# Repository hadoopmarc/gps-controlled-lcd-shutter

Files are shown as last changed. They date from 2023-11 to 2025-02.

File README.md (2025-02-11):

# gps-controlled-lcd-shutter

## Introduction

The GPS-controlled LCD shutter is used for photography of bright meteors. Traditionally, periodic shutters are applied in multi-station photography for aiding the calculation of the atmospheric trajectory and velocity of a meteoroid. The controlling system documented in this git repository adds 1 Hz time markers to the waveform driving an LCD shutter. These markers are synchronized with the highly accurate time signal of a GPS module. The markers function as additional reference points for comparing records from multiple stations. The technique was pioneered by the Ondřejov Observatory in the Czech Republic, see: [https://link.springer.com/article/10.1007/s11038-017-9511-z](https://link.springer.com/article/10.1007/s11038-017-9511-z).

The required pattern for obstructing the light passing through the camera lens is visible from the photograph below (courtesy of the Astronomical Institute of the Academy of Sciences of the Czech Republic).

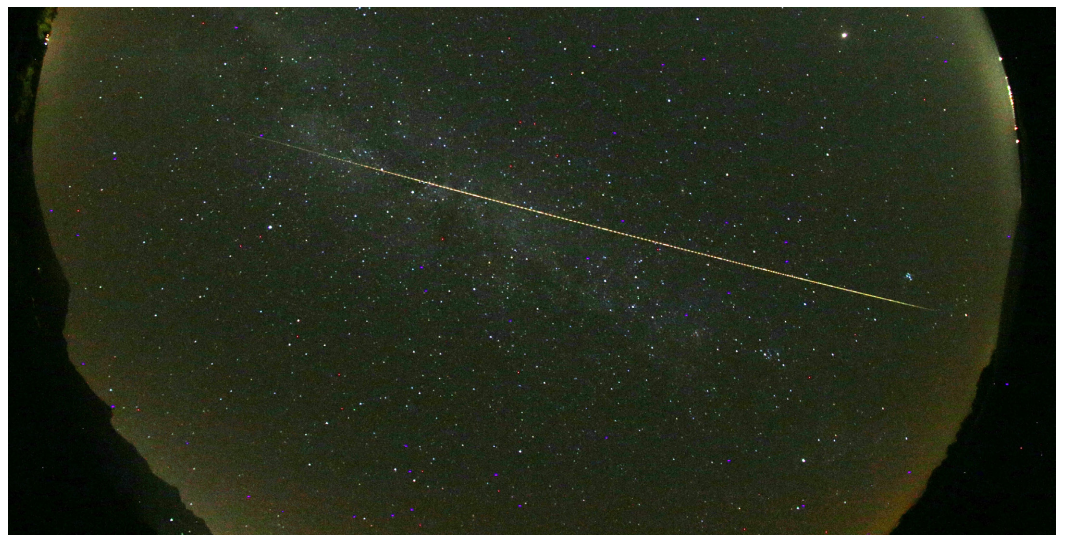
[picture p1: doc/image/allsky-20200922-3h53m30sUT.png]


## Reference design

When using an LCD shutter to realize the required pattern one needs an LCD opaqueness waveform represented as signal I in the figure below. The end of a long part of the meteor trail - or the rising edge of the first pulse of a pulse train in signal I - occurs a N + 2/32 seconds exactly.

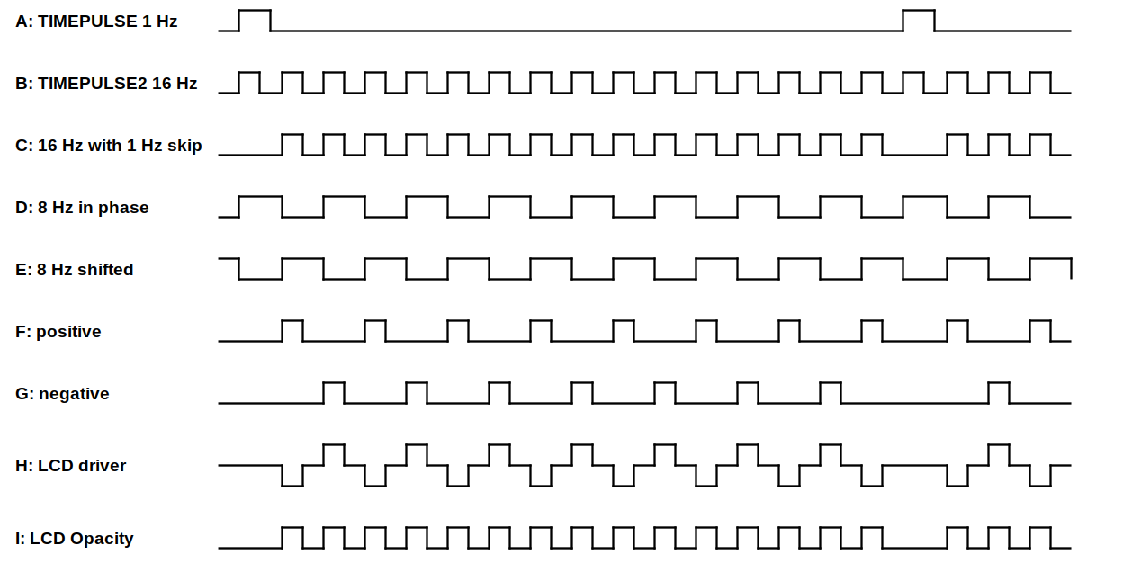
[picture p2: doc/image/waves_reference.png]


The waveform required to drive the LCD shutter has both a 16 Hz signature for the periodic interruptions and a 1 Hz signature for the second markers. The Ublox Neo-M8T SoC is able to deliver both signals with high precision on its TIMEPULSE and TIMEPULSE2 outputs (signals A and B). Because of this high precision, the design with Neo-M8T is designated as the reference design.

Apart from the frequencies involved, there are additional requirements for driving an LCD shutter:

- although an LCD shutter becomes opaque when a voltage is put on it in either direction, it is advised to change the polarity of the applied voltage with each cycle to avoid degradation of the display (signal H)
- upon switching, the shutter draws a relatively high peak current of 28 mA during a short time

These requirements make that the LCD-shutter is better not driven by logical outputs directly. Rather, the reference design applies opamps to convert the logical signals into +/- 12V with a sufficiently low output impedance, see the top part of the electronic circuit below. The final opamp adds the inverted signal F to the signal G to create signal H. The electronic circuit for the final opamp includes a variable resistor RV1 to set the "inactive" output voltage to exactly 0V for maximum transparency of the LCD shutter.

For converting signals A and B into signals F and G, a few CMOS NAND ports and a D-flipflop are applied. Note that the 1 Hz signal is also fed into the reset port of the flipflop to have the edges of the 8 Hz signals D and E coincide with the rising edge of the 1 Hz signal.

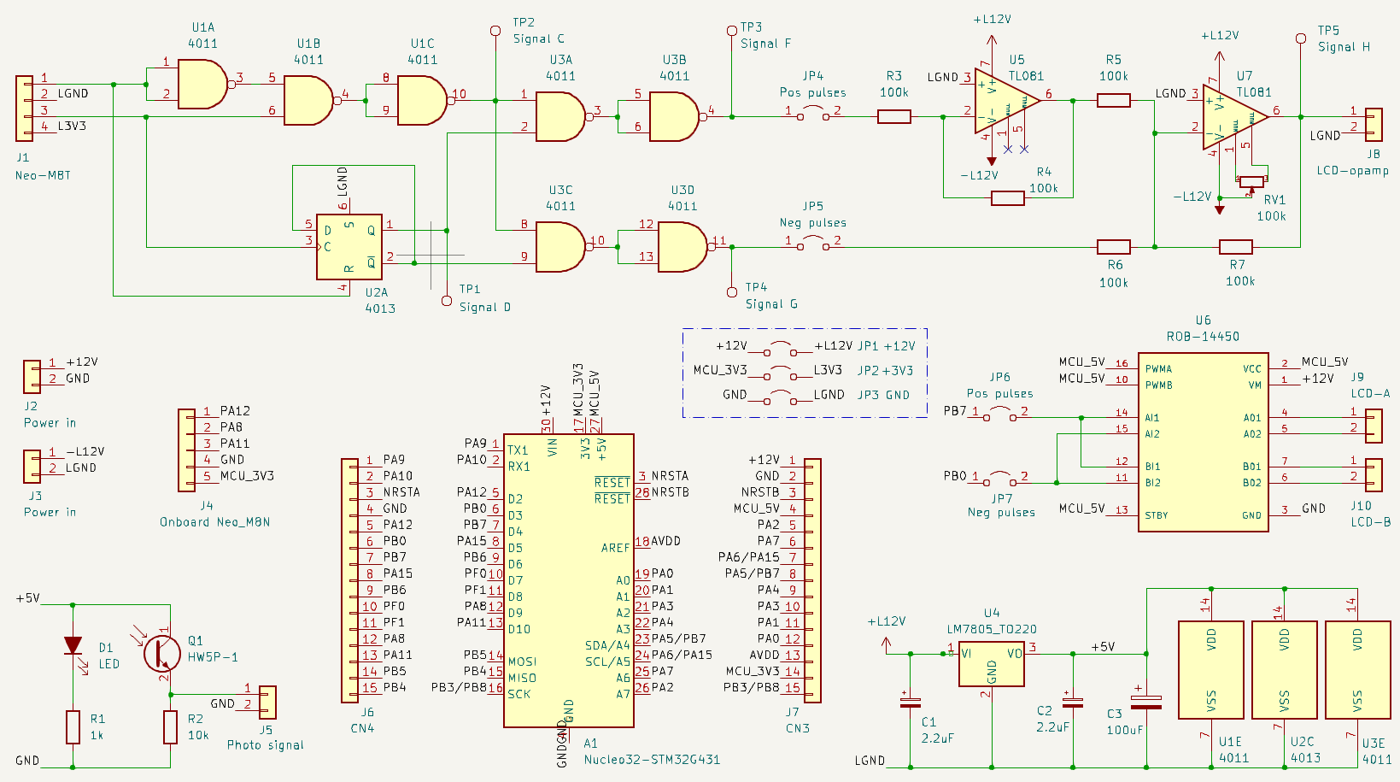
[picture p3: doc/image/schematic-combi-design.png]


## Optimized design

Although the reference design guarantees a high timing precision, it has significant drawbacks:

- the Neo-M8T is 10 times more expensive than its more nimble Neo-M8N sibling and dominates the production costs of the system
- the Neo-M8T is not available on a breakout board with the TIMEPULSE and TIMEPULSE2 output signals, so this requires high-precision soldering on 1 mm spaced SMD output pins
- the opamp circuit requires positive and negative power supplies
- the opamp circuit is hard to get stable and can only barely supply the peak current of the LCD shutter

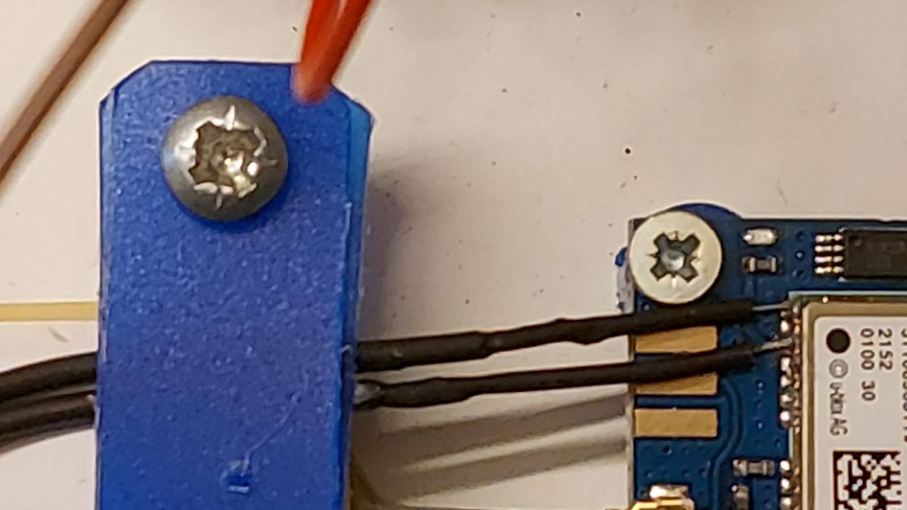
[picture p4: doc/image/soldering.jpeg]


Presenting the reference design to two different audiences resulted in valuable feedback to optimize the design:

- the required waveforms can also be produced by a microcontroller such as the Arduino board, by only using the 1 Hz output signal of a GPS module and using the internal, less precise clock of the microcontroller to obtain the 16 Hz timing information (see [this contribution to the repository](https://github.com/hadoopmarc/gps-controlled-lcd-shutter/commit/29299f46e7cd1bd2d8dd73f03644191cccfc6193)). Now, the cheaper Neo-M8N suffices to provide the 1 Hz timing data.
- an H-bridge module - often used to drive a DC motor - seems also suitable to drive the LCD shutter. An H-bridge only requires a positive power supply and can deliver high output currents.

This feedback resulted in the final optimized design, displayed in the electronic circuit diagram below. As the LCD shutter is already driven with a 16 Hz frequency, the H-bridge PWM duty cycle has a fixed setting of 100%. An H-bridge has two modes for a low output voltage, see the truth table below: short circuit the output pins ("Short brake" in motor terms) or disconnect the output pins ("Free run until frictional stop" in motor terms). It turns out that the LCD shutter needs the short circuit so that it can release its internal charge/polarity and become transparent as fast as possible.

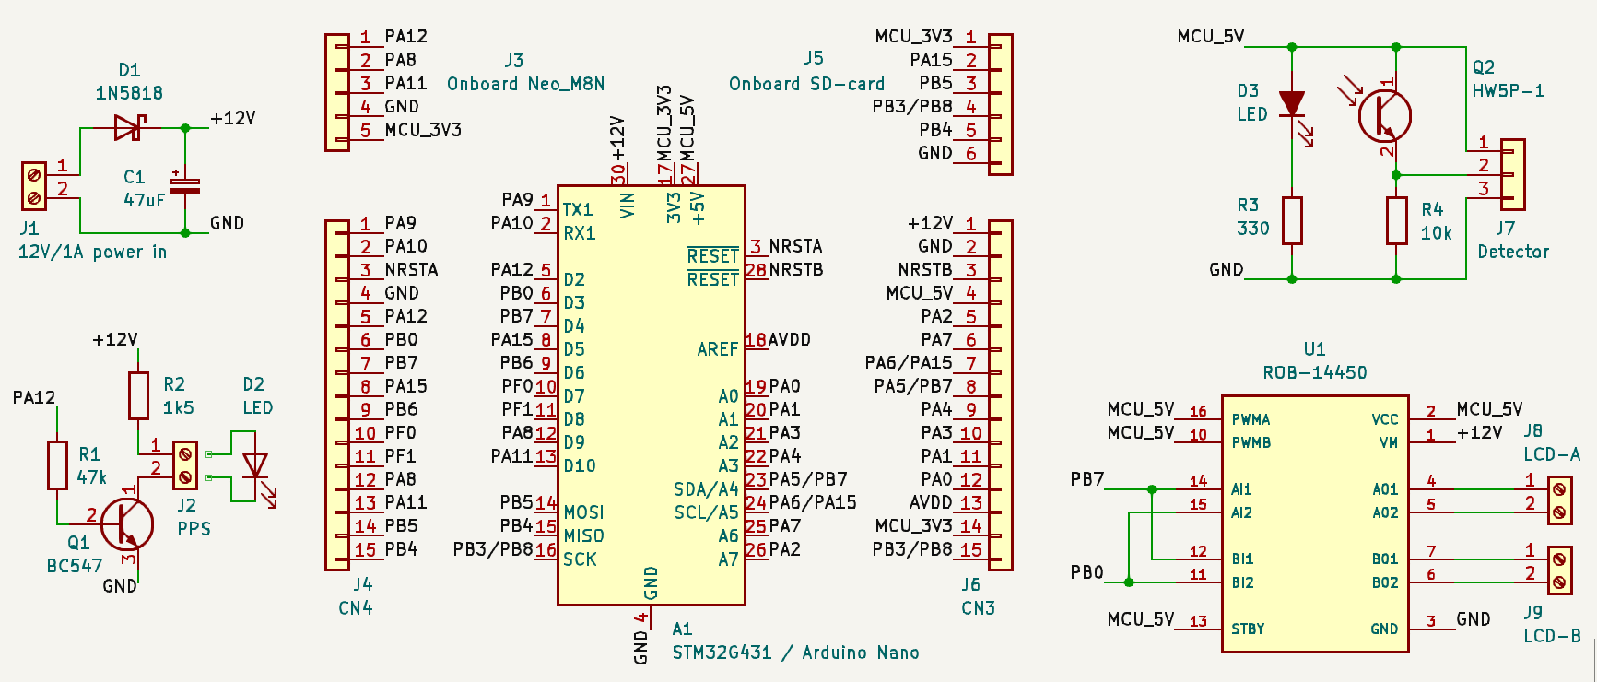
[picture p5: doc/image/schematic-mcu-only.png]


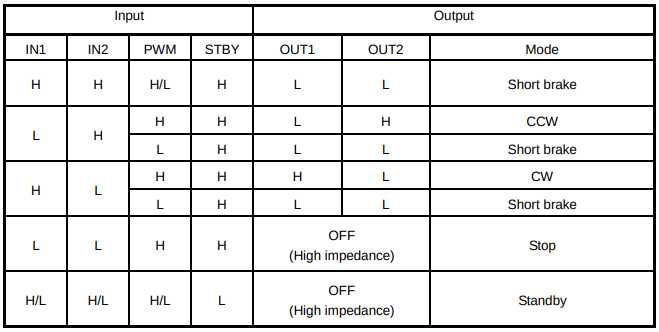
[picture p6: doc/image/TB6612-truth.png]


The required input signals to the H-bridge are displayed in the waveform diagram below. Also in this design, the end of a long segment in the meteor trail - or the rising edge of the first pulse of a pulse train in the LCD opacity signal - occurs a N + 2/32 seconds exactly. After all, the long segment in the meteor trail has a duration of 3/32 second, but the GPS second pulse occurs after 1/32 second from the start of the long segment.

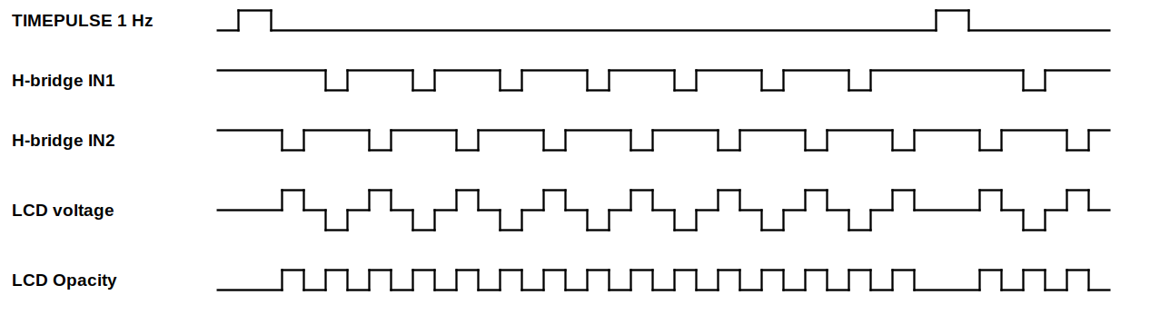
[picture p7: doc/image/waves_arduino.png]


## Validation of the designs

Proper operation of both designs can be validated with an [Arduino Oscilloscope](./doc/arduino-scope.md) and the small LED + phototransistor setup of the lower left part of the electronic circuit diagram.

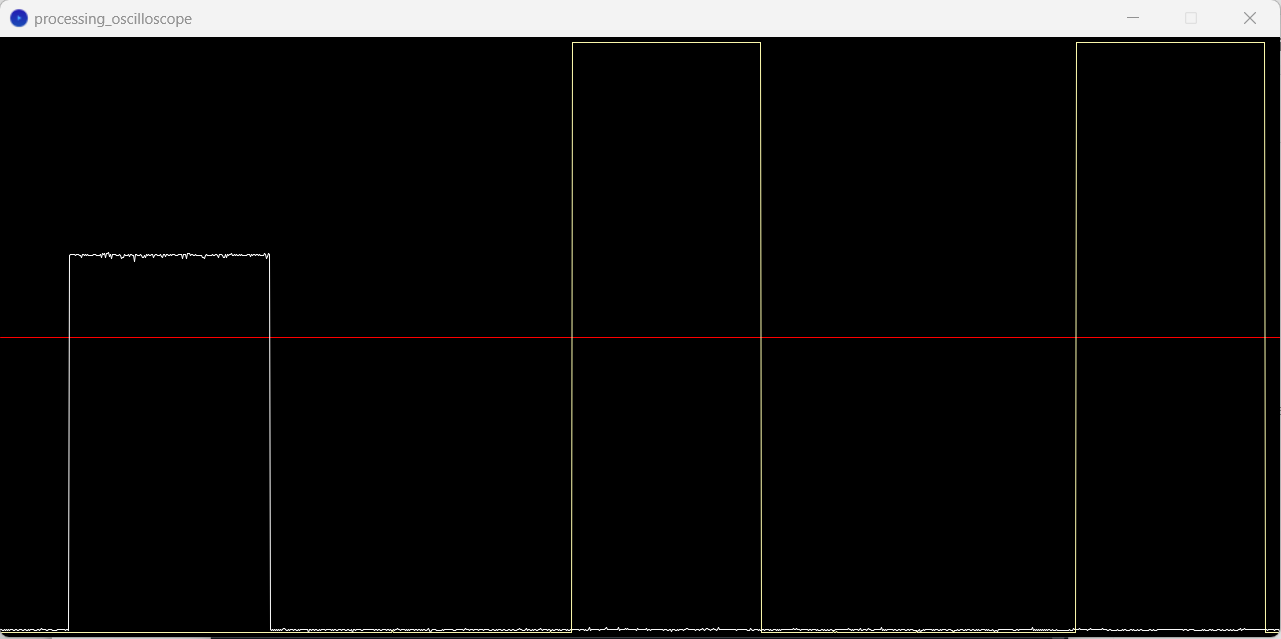
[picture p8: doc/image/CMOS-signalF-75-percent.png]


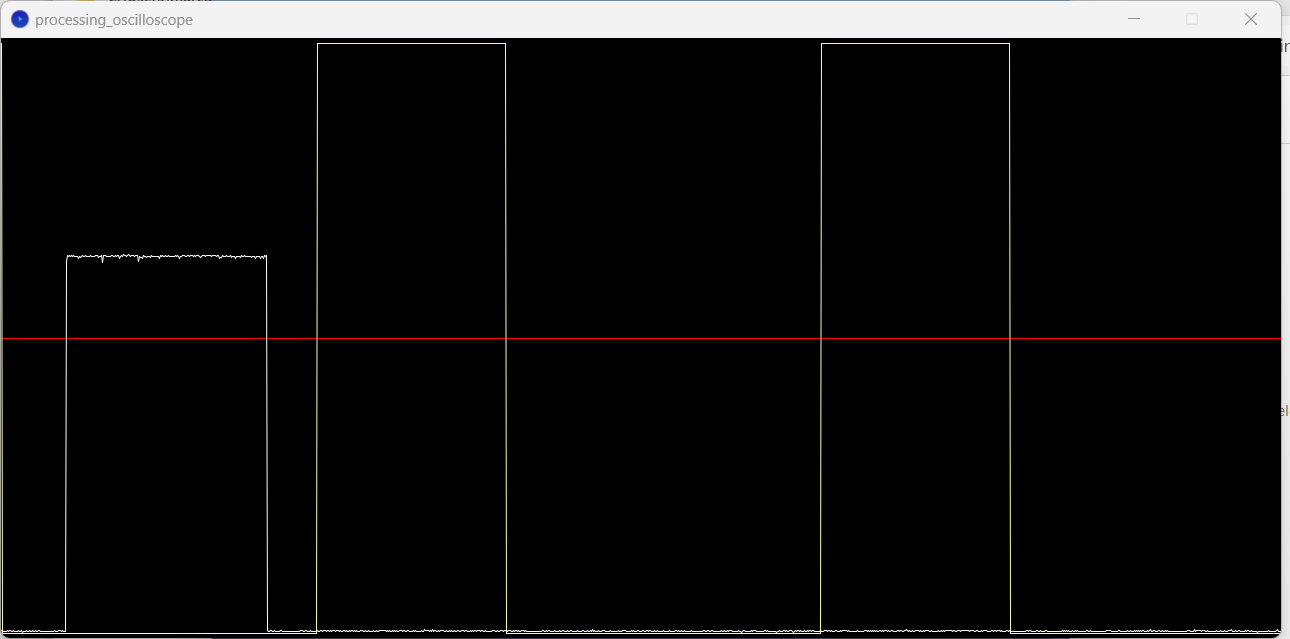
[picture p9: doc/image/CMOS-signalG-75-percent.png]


The two oscilloscope diagrams above display signals F and G (yellow lines) simultaneously measured with the Pulse Per Second signal of the Neo-M8T module  (configured with a pulse duration of 50 ms). The pulse duration of signals F and G is 46875 ms (16 Hz with a duty cycle of 75% in case of a missing GPS satellite lock). The first diagram shows that the pulse at the start of a second is missing, as required.

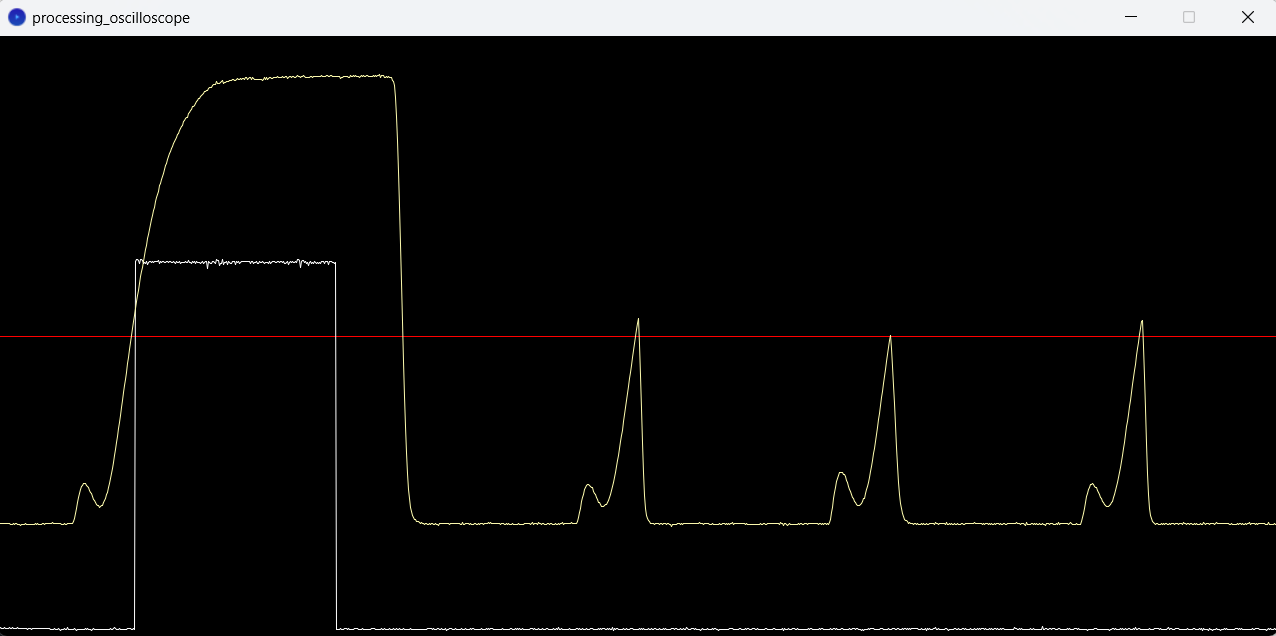
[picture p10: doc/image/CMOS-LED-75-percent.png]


In this image the yellow line represents the light throughput of the LCD shutter while driven by the reference design. The light is interrupted (sharp falling edges) at the start of a driver pulse (pulses not visible). There is no sharp falling edge coinciding with the rising edge of the GPS Pulse Per Second signal and the shutter can fully open. Note that these measurements were made with the cheap first generation LC-TEC shutters and that the measured opening response is consistent with [Figure 8.6 of their specifications](https://www.lc-tec.se/wp-content/uploads/2019/05/FOS_FOS-AR-specification-1602.pdf). Also note that the light transmission of the odd and even pulses is not exactly equal, indicating that the opamp driver circuit is not exactly balanced.

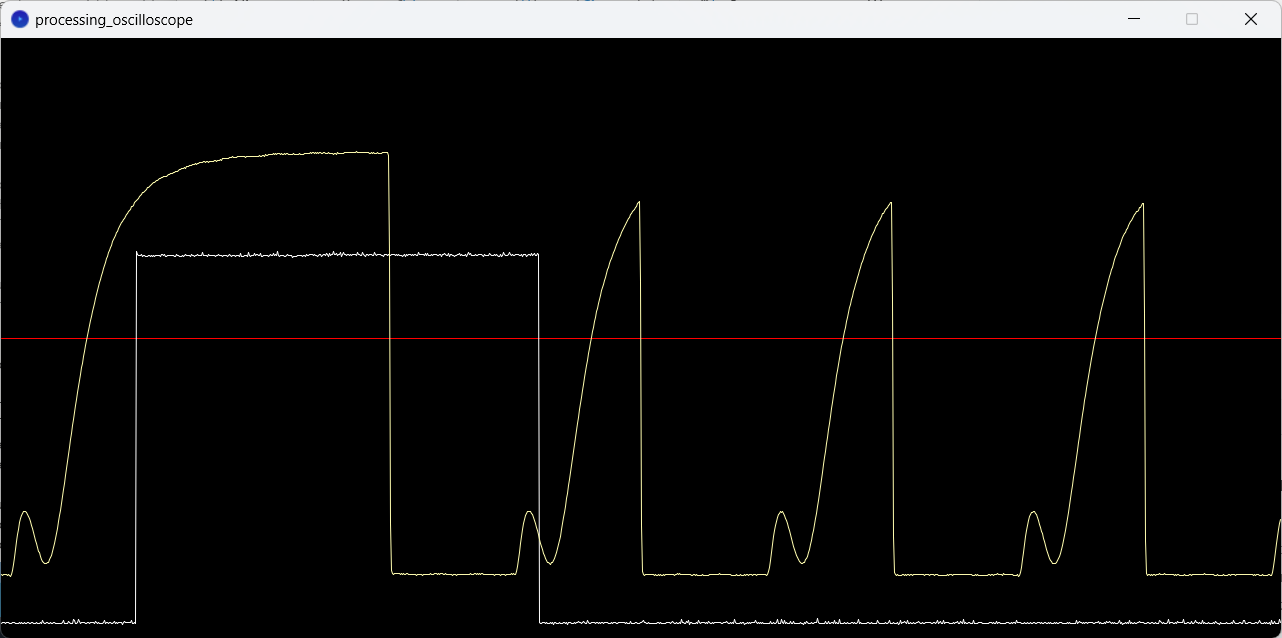
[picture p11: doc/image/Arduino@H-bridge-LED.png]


Again the light throughput against the GPS Pulse Per Second signal, but now for the optimized design with a Neo-M8N GPS module, an Arduino Nano and an H-bridge. Now, the GPS pulse has a duration of 100 ms and the duty cycle of the driver pulses is 50%, which gives the LCD-shutter more time to open than in the earlier image for the reference design.

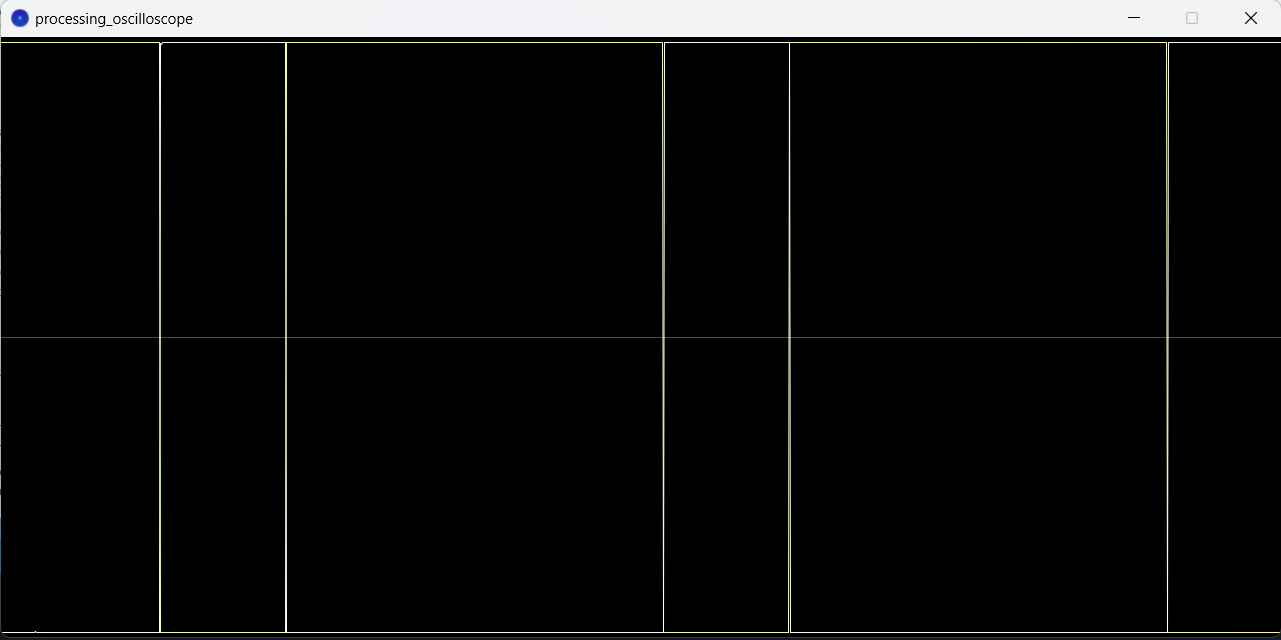
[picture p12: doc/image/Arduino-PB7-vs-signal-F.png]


This picture looks boring, but its significance is high. It displays the reference and optimized designs operating simultaneously with independent GPS receiver modules, both with a satellite lock. The white line shows signal F from the reference design, while the yellow line shows the H-bridge IN1 signal of the optimized design. This demonstrates that within the measuring accuracy of the oscilloscope used, the edges of the signals coincide.

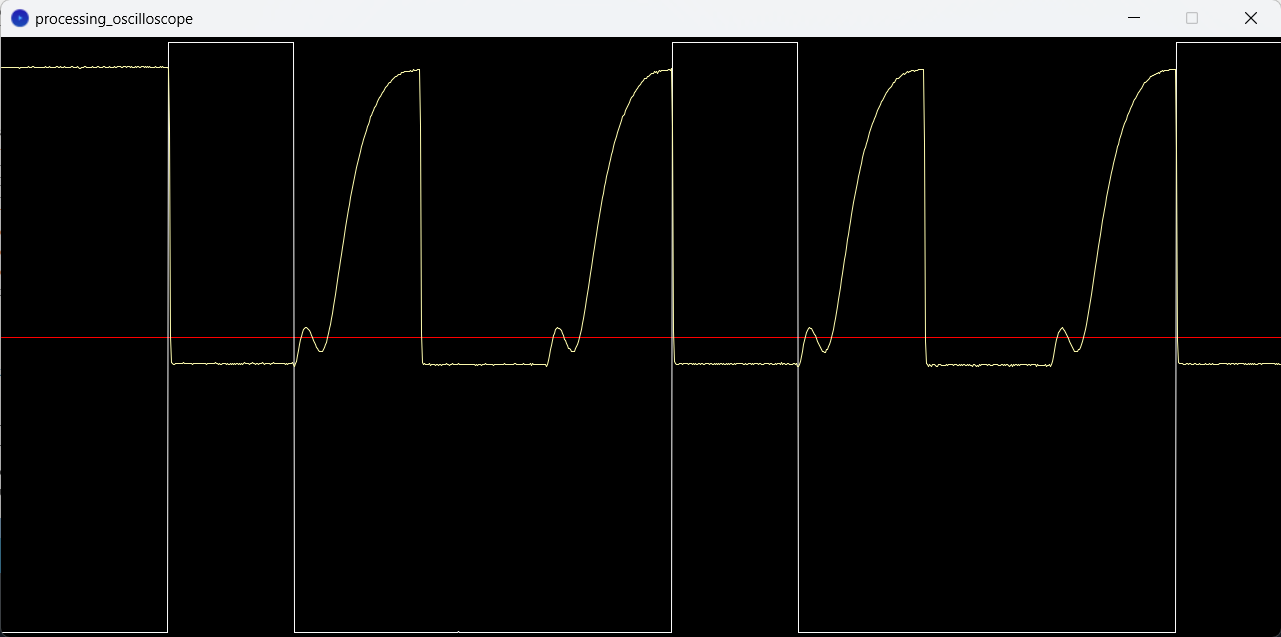
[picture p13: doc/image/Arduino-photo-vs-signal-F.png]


This picture is a more attractive-looking variation on the picture above, again combining measurements from two independently operating setups. Here, signal F from the reference design (white line) is combined with the light throughput of the LCD shutter driven by the optimized design (yellow line). Also, here the opening and closing instances of the LCD-shutter nicely coincide with the falling and rising edges of signal F. Note that the measurements in the last two images were made with the electronic circuits built on a printed circuit board, while previous more noisy images were from circuits built on a breadboard. Also, a different phototransistor and LCD-shutter were used, explaining the slightly different light throughput curve, compared to the earlier images.

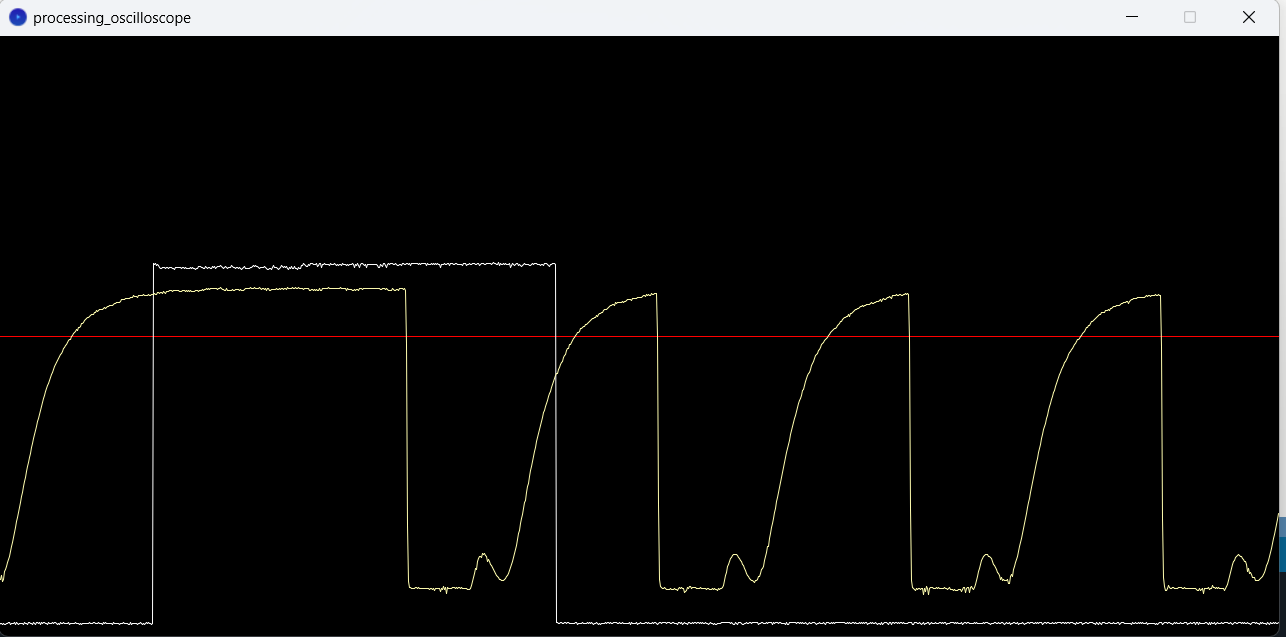
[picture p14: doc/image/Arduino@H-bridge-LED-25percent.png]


Starting from version 0.2.0 the electrical shut percentage can be configured to compensate for LCD shutters that fail to reopen fast enough to truthfully follow the electrical signals. In this oscilloscope screenshot a shut percentage of 25% is applied to a cheap LCD shutter, resulting in an open/closed ratio of roughly 50/50. White line is the GPS signal.

## Phase measurements in the optimized design

Apart from validation measurements of the output signals of the electronic circuits, it is also possible to use internal measurements from the microcontroller as a form of validation. The controlling software generates the pulses using timer interrupts. The timer period is chosen such that the end of a pulse train occurs at a phase difference Δt just before the ideal time instance required by the nanosecond precision GPS time. For an Arduino Nano microcontroller the timer has a limited resolution and as a result Δt has a stable value between 0 and 128 microseconds. How to monitor this phase difference and phase stability is described [here](./doc/arduino-programming.md).

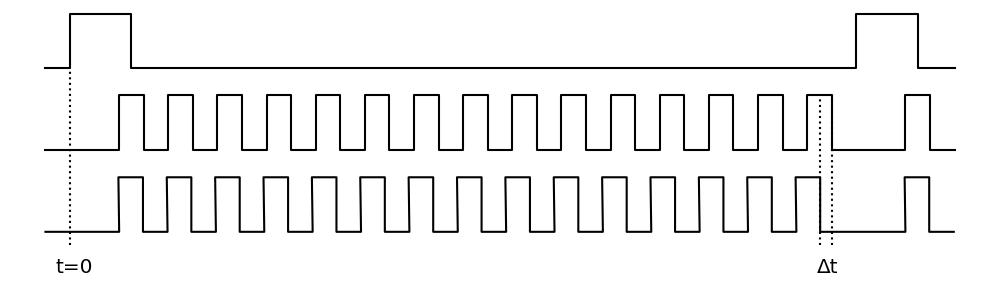
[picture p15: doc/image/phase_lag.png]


## Further documentation

- [Programming the Arduino Nano module](./doc/arduino-programming.md)
- [Measuring with an Arduino Oscilloscope](./doc/arduino-scope.md)
- [Datasheets of system components](./doc/datasheet.md)

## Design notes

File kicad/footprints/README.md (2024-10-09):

# Custom Footprints for the PCB

This folder contains custom footprints for producing the PCB of the GPS LCD shutter. They should be imported in KiCad. When using KiCad in Ubuntu they are put at the ${KICAD8_3RD_PARTY} location, which is short for ~/snap/kicad/current/.local/share/kicad/8.0/3rdparty.

The footprints for the Neo M8N module and the SDcard reader do not have associated symbols. If you want them to use in other projects, you can simply take a standard header pin connector from the KiCAD library as symbol.

In addition to the custom footprints in this git repository, you need to download and import the custom model and footprint of the H-bridge module from: [https://www.snapeda.com/parts/ROB-14450/SparkFun%20Electronics/view-part/](https://www.snapeda.com/parts/ROB-14450/SparkFun%20Electronics/view-part/).

After importing all footprints in KiCad, the relevant part of your directory structure looks like:

```bash
~/snap/kicad/current/.local/share/kicad/8.0/3rdparty$ tree .
.
├── Neo-M8N_Module.pretty
│   └── Neo-M8N_1x05_P2.50mm_Horizontal.kicad_mod
├── SDcard_IPC_breakout.pretty
│   └── SDcard_IPC_breakout_1x06_P2.54mm_Vertical.kicad_mod
├── TB6612_Module_ROB-144450.pretty
│   └── TB6612_Module_ROB-14450.kicad_mod
├── Variants.pretty
│   └── TerminalBlock_RND_1x02_P5.00mm_Horizontal_Small_Courtyard.kicad_mod
└── TB6612_module_ROB-14450
    ├── how-to-import.htm
    ├── ROB-14450.kicad_sym
    └── ROB-14450.step

5 directories, 6 files
```

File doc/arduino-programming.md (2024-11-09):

# Arduino programming

Programming the Arduino Nano can already be done before it is mounted on the PCB, but it is also possible to do it afterwards. Also, future updates of the software can be uploaded without removing the Arduino from the PCB. Once the Arrduino is programmed, the program is stored in its flash memory. Whenever you restart the Arduino, it will run the program from the flash memory.

## Installing the Arduino IDE

The Arduino IDE is available for all popular operating systems. You install it from one of the package managers supported by your OS or you can install it from the [Arduino download page](https://www.arduino.cc/en/software), whatever you trust better. Some OS may require to install the Java Runtime Enviromnemt first. Also here, install it from one of the package managers or get the full JDK17 from [https://www.oracle.com/java/technologies/downloads/](https://www.oracle.com/java/technologies/downloads/).

Most likely you use Microsoft Windows and you can simply install the Arduino IDE legacy version (1.8.x) from the Microsoft Store, which includes a copy of the Java JRE. The Arduino program in this git repository was only tested with this legacy version.

## Downloading the LCD shutter driving software

The latest software for the GPS-controlled LCD shutter driver can be downloaded from:

[https://github.com/hadoopmarc/gps-controlled-lcd-shutter/tags](https://github.com/hadoopmarc/gps-controlled-lcd-shutter/tags)

Select the version you need, supposedly the latest version, download the source code archive and extract it at some place where it can easily be found back. Of course, if you know how to use git and want to contribute to the repository, you can git clone the repository instead of downloading the archive.

## Programming the Arduino

Programming the Arduino Nano should now be so simple as:

1. connect the Arduino to your PC/laptop using a USB-cable
1. open the local file 'gps-controlled-lcd-shutter/arduino/waveform-h-bridge/waveform-h-bridge.ino' with the Arduino IDE. This will open three files in separate tabs. The file gps_shutter_control.cpp contains the actual program. The two other files prepare the Arduino for later extensions.
1. in the file 'waveform-h-bridge.ino' manually edit the required SHUT_PERCENTAGE for the connected LCD-shutter system
1. select the Arduino Nano from the "Tools / Board / Arduino AVR boards" menu option
1. select the right COM-port from the "Tools / Port" menu option (if no COM port is marked as Arduino Nano, disconnect and reconnect the Arduino to discover the right COM port)
1. push the "Upload ->" button in the taskbar. If the compilation fails, please contact the repository owner. If the upload fails, disconnect and reconnect the Arduino and try again.

The microcontroller on an Arduino board may have so-called [lock bits](https://microchip.my.site.com/s/article/Use-of-Lock-Bits-in-AVR-devices)or [fuses](https://circuitdigest.com/microcontroller-projects/understanding-fuse-bits-in-atmega328p-to-enhance-arduino-programming-skills) set such that it cannot be programmed with the Arduino IDE anymore. The lockbits can be reset by following the [Arduino bootloader burning procedure](https://docs.arduino.cc/built-in-examples/arduino-isp/ArduinoISP/#recap-burn-the-bootloader-in-8-steps). Resetting fuses requires 12V programming with a [more convoluted setup](https://www.instructables.com/HV-Rescue-Simple/) and is totally impractical for an Arduino Nano with a soldered SMD microcontroller.

## Checking the logs

Once the uploaded program runs, it produces log statements over the serial interface. You can check these by opening the serial monitor of the Arduino IDE (far right button on the taskbar). On powering up the PCB, the GPS-module needs about half a minute to lock on one or more satellites and after that the LCD shutter program needs 10 GPS pulses before generating the second markers in the driver output towards the LCD shutter. During that time the serial monitor only shows:

```log
    Waveform-H-bridge version: 0.x.y
    Electrical blocking percentage: 50%
    Configuration completed
    Stabilizing...
```
After this, the serial monitor shows a few log lines related to the preliminary calibration of the CPU clock frequency relative to the Pulse Per Second (PPS) signal from the GPS module. These lines have the following format:

```log
    Micros: 10 10014560
    CPU: 16023260
    Block: 7822 ticks
```
The CPU frequency should be 16 +/- 0.08 MHz (large error margins because of the cheap ceramic resonator used on the Arduino module). The CPU frequency should only show minor variations during operation. The block ticks refer to the number of required timer events during one half wave (block pulse) of the driver output. This number is derived from the measured CPU frequency and should also show only minor variations.

The calibration, including logging, is repeated every 60 seconds to account for changes in the operating conditions of the Arduino (power voltage, temperature).

In addition to the calibration every minute, the serial monitor shows the phase stability of the driver pulse train, relative to the GPS PPS signal. The log lines look something like the text below, every second:

```log
    LCD phase: 0 277 9 1684
    LCD phase: 0 3 0 12
    LCD phase: 0 4 0 12
```

These are variables used in synchronizing the timer outputs derived from the MCU clock with the GPS PPS signal. The successive variable on a log line are, just before synchronization starts:

1. iIsr, the number of timer interrupts (0-31) since a GPS pulse
1. observedTicks, the number of timer ticks of 4 microsecond
1. oldHalfWave, the index in the range of pulse train parts (0-31) relative to the previous synchronization
1. oldTCNT1, the value of the timer that drives the start of switching to the next part of the pulse train

During stable operation, iIsr and oldHalfwave should be zero and observedTicks should be small, indicating that synchronization takes place immediately after the incoming GPS pulse. The difference between oldTCNT1 and observedTicks is the accumulated phase differerence during one second in "ticks" of 4 microseconds. This should be a figure between 0 and 32 ticks (meaning between 0 and 128 microseconds). In the example log lines above, only the first line shows a large phase difference, because the driver pulse train was not synchronized to the GPS signal before that time.

The logging described above is the logging during normal operation. There are two additional log messages that can occur and they indicate possible failures in the system:

1. "Unexpected GPS pulse arrival. Deviation: 21432 microseconds". This indicates instable operation of the GPS module. This can have all kinds of causes, including a too weak GPS signal, an instable power supply, interference from other systems, hardware failure, etc.
1. "Avoidance triggered". This indicates that synchronization starts before the pulse train of the previous second has finished. Possible causes are fast changes in the environment temperature and a hardware failure of the Arduino module.
Fast changes in temperature can be forced by blowing a hair dryer at the Arduino module. Blowing the dryer makes the MCU clock slow down and the pulse train of the previous GPS pulse train is not completed before the next GPS pulse arrives, resulting in an iISR==1. Blowing the dryer longer, one can even enter the state where the phase compensation has detected the arrival of a new GPS pulse before the old pulse train has completed: this triggers the avoidance warning message.

## Bootloader burning on Arduino

Cloned Arduino Nano modules ordered from China may have the so-called "Old bootloader". Although the Arduino IDE offers the option to upload scripts to modules with the "Old bootloader" instead of the default boatloader, this is annoying from a maintenance perspective. The Arduino bootloader burning procedure described [here](https://docs.arduino.cc/built-in-examples/arduino-isp/ArduinoISP/#recap-burn-the-bootloader-in-8-steps) has clear instructions for how to use the Arduino IDE for replacing the bootloader using a second Arduino module, but the wiring instructions are incomplete. Below, a description is added of an Arduino module's ISCP pins as well as their orientation.

### ISCP pins ([source](https://docs.arduino.cc/resources/pinouts/A000066-full-pinout.pdf))

1. CIPO <--> CIPO/D12
2. +5V <--> +5V for Uno and Nano, some boards need +3V
3. SCK <--> SCK/D13
4. COPI <--> COPI/D11
5. RST <--- D10
6. GND <--> GNDS

Learnt from reading several descriptions:

- the RST ISCP pin can only be used as input and is connected to D10 of the programmer board
- other ISCP pins can be used as both input and output
- CIPO connected to CIPO, COPI to COPI (no crosswiring as for serial RX/TX)
- older Arduino descriptions call the ISP pins MISO/MOSI, newer ones CIPO/COPI (controller/peripheral vs master/slave)

### ISCP Header orientation

Arduino modules may have the ISCP connector marked with a `1`, an `ISCP` mark, or both. Pin numbers with respect to these marks go like:

|| | | | | |
||-|-|-|-|-|
|<td colspan=2>mark</td>|
||6|5|&nbsp;&nbsp;&nbsp;&nbsp;&nbsp;&nbsp;&nbsp;&nbsp;&nbsp;&nbsp;&nbsp;&nbsp;&nbsp;&nbsp;&nbsp;&nbsp;&nbsp;|1|2|
||4|3| |3|4|
||2|1| |5|6|
||||<td colspan=2>mark</td>|

- my Arduino Nano clone has a mark "1" with pin 1 facing the edge of the board
- official Arduino Uno R3 has a mark "ISCP" with pin 1 facing the center of the board
- marking of clones may differ from legitimate boards

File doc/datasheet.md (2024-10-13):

# Datasheet links for applied electronic components and modules

## Relevant to both designs
[Arduino Nano](https://docs.arduino.cc/resources/datasheets/A000005-datasheet.pdf)  
[TB6612FNG](https://toshiba.semicon-storage.com/info/TB6612FNG_datasheet_en_20141001.pdf?did=10660&prodName=TB6612FNG)  
[NEO-M8 Datasheet](https://content.u-blox.com/sites/default/files/NEO-M8-FW3_DataSheet_UBX-15031086.pdf)  
[NEO-M8 Hardware Integration Manual](https://content.u-blox.com/sites/default/files/NEO-M8_HardwareIntegrationManual_%28UBX-13003557%29.pdf)  
[U-blox8 Configuration Guide](https://content.u-blox.com/sites/default/files/products/documents/u-blox8-M8_ReceiverDescrProtSpec_UBX-13003221.pdf)  
[SD-card reader TF SPI](https://randomnerdtutorials.com/esp32-microsd-card-arduino/)  

## Specific to combi design
[CD4011B Quad NAND gate](https://www.ti.com/lit/ds/symlink/cd4011b.pdf)  
[CD4013B Dual D-type flipflop](https://www.ti.com/lit/ds/symlink/cd4013b.pdf)  
[CD4030B/CD4070B Quad XOR gate](https://www.ti.com/lit/ds/symlink/cd4030b.pdf)  
[TL074 Quad low-noise FET-input opamp](https://www.ti.com/lit/ds/symlink/tl074.pdf)  
[7805 5.0V Voltage regulator](https://www.ti.com/lit/ds/symlink/lm78l.pdf)  
[NEO-M8T datasheet](https://content.u-blox.com/sites/default/files/documents/NEO-LEA-M8T-FW3_DataSheet_UBX-15025193.pdf)  

## Optical shutter and testing
[LCtec standard LCD shutter 25 ms](https://www.lc-tec.se/wp-content/uploads/2019/05/FOS_FOS-AR-specification-1602.pdf)  
[LCtec fast LCD shutter 0.8 ms](https://www.lc-tec.se/wp-content/uploads/2019/05/X-FOSG2_X-FOSG2-AR-specification-1602.pdf)  
[Adafruit HW5P-1 phototransistor](...)

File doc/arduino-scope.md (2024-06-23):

# Measuring Digital Signals with an Arduino Oscilloscope

Checking the proper working of an electronic circuit that produces and outputs
various signals (time dependent voltages), requires an oscilloscope or digital analyzer. For the low frequency control signals in the GPS-controlled LCD shutter project it is possible, though, to program an Arduino microcontroller as an oscilloscope.

The oscilloscope scripts in this project are based on an original project, published [here](https://www.instructables.com/Arduino-Oscilloscope-poor-mans-Oscilloscope/).

## Overview

Using the Arduino as an oscilloscope requires a dedicated Arduino board
that runs a measuring script, see the figure below. So, when your circuit to be measured contains an Arduino itself, the total setup involves two Arduino boards.
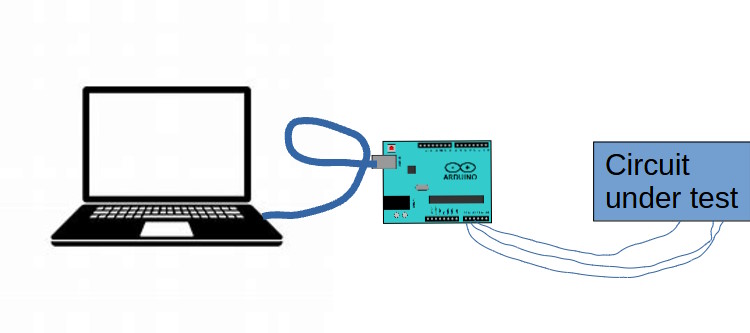
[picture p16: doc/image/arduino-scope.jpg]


To connect the Arduino scope to the circuit under test, three wires are needed.
One wire connects the ground planes (GND). The remaining two wires carry the
signals to be measured. They run from the A0 and A1 analog input ports of
the Arduino scope to two measuring points on the circuit under test.

The PC/laptop runs an oscilloscope display program (to be explained later)
and triggers on the A0 signal only. So, it is a good idea to have the lower
frequency signal on the A0 port of the Arduino oscilloscope.

| ⚠️⚠️⚠️ WARNING ⚠️⚠️⚠️                                                           |
|:--------------------------------------------------------------------------------|
| Be sure that: -0.5V < `input voltage` < +5.5 V, or your Arduino may get damaged |

## Programming the Arduino

The recipe for programming the Arduino with a measuring the script is the same as [programming it with the LCD-shutter driver script](./arduino-programming.md). The only difference is the file location: 'gps-controlled-lcd-shutter/arduino/oscilloscope/oscilloscope.ino'. After uploading the script you will see the TX LED on the Arduino board lighting up continuously, because it sends new measurements all the time over the USB serial link.

## Installing the Processing IDE

The Processing IDE is a simple, but multi-platform programming environment that is suitable to use together with the Arduino IDE, because they share the design philosophy and support the same basic c language. Moreover, an example script for an oscilloscope was already available, see the link in the introduction.

The Processing IDE can be downloaded [here](https://processing.org/download). It is a portable archive (for use on managed PC's in education), so installation on Windows involves:

- unpack the zip file somewehere in your Home area, e.g. C:\Users\Name\Lib
- to start the IDE, double-click on `processing-4.3\processing.exe`
- optionally, by right-clicking on `processing-4.3\processing.exe` you can add attach it to the Microsof Windows start menu
- optionally, when double-clicking on a .pde file, you can select `processing-4.3\processing.exe` as the preferred program to open .pde files.

## Running the Oscilloscope Processing Script

To run the oscilloscope script from the GPS-controlled LCD shutter, find the file `gps-controlled-lcd-shutter\arduino\processing_oscilloscope\processing_oscilloscope.pde` and open it. Wait before you run the script and follow these steps:

- switch to the Arduino IDE running the oscilloscope measuring script and display the list of active COM ports. Note the ordinal number in this list (starting from 0) of the COM port that connects to the Arduino (showing a ✔). So, if there is just one COM port active, this ordinal number is `0`. Now close the Aruino IDE, freeing the COM port for other applications on your laptop.
- switch back to the Processing IDE and scroll to line `43`. Now, in the code part `Serial.list()[1]` replace the `1` in this fragment with the ordinal number noted in the previous step, if needed
- now you can push the RUN button of the Processing IDE and after a while a graphic window will pop up, showing the signals of the circuit under test according to the wires connected to the measuring Arduino
- once the signals are present on the display it is possible to freeze the signals by pushing the `p` button (pause). Pushing the `p` again allows new measurements to come in. The pause mechanism uses a 0/1 transition on the A0 input port of the Arduino as a trigger and it also shows some part of the signal preceding this trigger
- For the GPS-controlled LCD shutter, the GPS PPS signal is the most suitable to use as the A0 trigger signal. On the PCB it is available as the D2 pin, the fifth pin of the J6 connector. Most interesting to measure with the A1 input of the measuring Arduino, is the J5 signal pin of the phototransistor measuring the light intensity visible through the LCD shutter.

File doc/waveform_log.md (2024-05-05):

# Validation using the waveform log

A typical log of the waveform sketch is listed farther down the file. It shows:

- the sketch needs 11 seconds for stabilizing before outputting LCD phase measurements

- it needs another 10 GPS pulses before it calibrates the CPU frequency from 16.000 MHz to 16.013 MHz and shifts to a different phase control pattern

To control the syncing of the LCD driving pattern with the GPS pulse, the sketch expresses the LCD phase in two ways:

1. phase = (iHalfWave * OCR1A + TCNT1) * TICK_MICROS, with OCR1A the number of timer ticks between timer interrupts (32 times per second), TCNT1 the number of timer ticks since the last interrupt and TICK_MICROS a value of 4 CPU clock microseconds

2. phase = observedDiff = t_s - lastGpsMicros, with t_s the current non-critical time of processing just before syncing the LCD driving pattern with the GPS pulse and lastGpsMicros the earlier measured time immediately after receiving a GPS pulse, both in CPU clock microseconds

The LCD phase measurements logged are:

- iIsr: for monitoring/debugging only. It is reset to zero directly after receiving a GPS pulse and incremented by one after each timer interrupt. Logging should show iIsr = 0 after stabilizing.
- observedTicks: observedDiff / TICK_MICROS. Logging shows a small value (< 10), when the Arduino only controls the LCD-shutter.
- oldHalfWave: the iHalfWave value just before the sync update. Logging should show iHalfWave = 0 after stabilizing.
- oldTCNT1: the TCNT1 value in TICK_MICROS just before the sync update. In perfect sync oldTCNT1 - observedTicks should be very small. However, the applied TIMER_SAFETY = 2 adds 2 * N_HALF_WAVE = 64 ticks to the ideal phase difference.

Before CPU calibration, a slower CPU frequency of 16.000 MHz is assumed instead of the actual 16.013 MHz. As result, the LCD driving pattern started at the previous GPS pulse, has already finished when the new GPS pulse arrives. This is consistent with the values around 14:41:27.207:

- iIsr = 0
- observedTicks = 3
- oldHalfWave = 0
- oldTCNT1: 232

So, in a period of 1 seconds, the LCD driving pattern gets ahead of the GPS pulse by (232 - 3) * TICK_MICROS = 916 microseconds. This is slightly more than expected from the end-to-end time difference measurement for CPU calibration: 20016004 in 20 seconds amounts to 800 micros per second. This has to do with the rounding required for OCR1A and the TIMER_SAFETY = 2 applied (2 * TICK_MICROS * N_HALF_WAVE = 256 microseconds).

After calibration of the CPU frequency at 14:41:34.249 logged LCD phase parameters remain stable and within specification.

14:41:13.634 -> Configuration of LCD shutter completed  
14:41:13.681 -> Stabilizing...  
14:41:25.185 -> LCD phase: 0 4 17 4899  
14:41:26.215 -> LCD phase: 0 3 0 231  
14:41:27.207 -> LCD phase: 0 3 0 232  
14:41:28.199 -> LCD phase: 0 3 0 232  
14:41:29.187 -> LCD phase: 0 3 0 232  
14:41:30.181 -> LCD phase: 0 3 0 232  
14:41:31.201 -> LCD phase: 0 3 0 232  
14:41:32.183 -> LCD phase: 0 3 0 232  
14:41:33.217 -> LCD phase: 0 3 0 232  
14:41:34.203 -> LCD phase: 0 3 0 232  
14:41:34.203 -> Micros: 20 20016004  
14:41:34.249 -> CPU: 16012802  
14:41:34.249 -> Block: 7816 ticks  
14:41:35.190 -> LCD phase: 0 3 0 39  
14:41:36.173 -> LCD phase: 0 3 0 40  
14:41:37.204 -> LCD phase: 0 3 0 39  
14:41:38.190 -> LCD phase: 0 3 0 39  
14:41:39.218 -> LCD phase: 0 3 0 39  
14:41:40.205 -> LCD phase: 0 3 0 39  
14:41:41.177 -> LCD phase: 0 3 0 39  
14:41:42.200 -> LCD phase: 0 3 0 39  
14:41:43.173 -> LCD phase: 0 3 0 39  
14:41:44.204 -> LCD phase: 0 3 0 39  
14:41:45.193 -> LCD phase: 0 4 0 39  
14:41:46.175 -> LCD phase: 0 3 0 40  
14:41:47.203 -> LCD phase: 0 3 0 39  
14:41:48.183 -> LCD phase: 0 3 0 39  
14:41:49.212 -> LCD phase: 0 4 0 39  
14:41:50.197 -> LCD phase: 0 3 0 40  
14:41:51.182 -> LCD phase: 0 3 0 39  
14:41:52.214 -> LCD phase: 0 3 0 38  
14:41:53.202 -> LCD phase: 0 3 0 39  
14:41:54.185 -> LCD phase: 0 3 0 39  
14:41:54.232 -> Micros: 40 40032004  
14:41:54.232 -> CPU: 16012802  
14:41:54.279 -> Block: 7816 ticks  
14:41:55.220 -> LCD phase: 0 3 0 38  
14:41:56.206 -> LCD phase: 0 3 0 39  
14:41:57.188 -> LCD phase: 0 5 0 40  
14:41:58.216 -> LCD phase: 0 3 0 40  
14:41:59.189 -> LCD phase: 0 3 0 39  
14:42:00.175 -> LCD phase: 0 3 0 39  
14:42:01.199 -> LCD phase: 0 3 0 39  
14:42:02.181 -> LCD phase: 0 3 0 39  
14:42:03.212 -> LCD phase: 0 3 0 39  
14:42:04.197 -> LCD phase: 0 3 0 39  
14:42:05.182 -> LCD phase: 0 3 0 39  
14:42:06.217 -> LCD phase: 0 3 0 39  
14:42:07.204 -> LCD phase: 0 3 0 39  
14:42:08.192 -> LCD phase: 0 3 0 39  
14:42:09.178 -> LCD phase: 0 3 0 39  
14:42:10.205 -> LCD phase: 0 3 0 39  
14:42:11.186 -> LCD phase: 0 3 0 39  
14:42:12.213 -> LCD phase: 0 3 0 39  
14:42:13.186 -> LCD phase: 0 3 0 39  
14:42:14.216 -> LCD phase: 0 4 0 39  
14:42:14.216 -> Micros: 60 60048004  
14:42:14.262 -> CPU: 16012801  
14:42:14.262 -> Block: 7816 ticks  
14:42:15.205 -> LCD phase: 0 3 0 40  
14:42:16.198 -> LCD phase: 0 4 0 39  
14:42:17.185 -> LCD phase: 0 3 0 40  
14:42:18.175 -> LCD phase: 0 4 0 39  
14:42:19.212 -> LCD phase: 0 3 0 40  
14:42:20.206 -> LCD phase: 0 3 0 39  
14:42:21.184 -> LCD phase: 0 3 0 39  
14:42:22.217 -> LCD phase: 0 3 0 39

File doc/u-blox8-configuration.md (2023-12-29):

# U-blox8 configuration

## Setup
- RPI400 with Raspbian 11 (bullseye)
- pygpsclient-1.4.6 on python-3.9.2
- USB/UART programmer module
- U-blox NEO-M8T module

The pygpsclient is only used for setting the UBX configuration variables, but is also useful to check the satellite fix on a specific geographic location. Note that on an RPI400 the client cannot keep up with showing NMEA messages in the console and the displayed UTC time starts lagging. This does not occur when the console is disabled in the view settings or the preset command "CFG-MSG - Turn ON minimum NMEA msgs" is issued from the UBX configuration window.

## Available configuration examples
The [U-blox8 configuration guide](https://content.u-blox.com/sites/default/files/products/documents/u-blox8-M8_ReceiverDescrProtSpec_UBX-13003221.pdf) gives the following examples for configuring the TIMEPULSE/TIMEPULSE2 outputs of the NEO-M8T module with the ubx protocol (section 19.5, page 74):

| ubx key           | ubx value 1 | ubx value 2 | comment |
| :------------     | ----------- | ----------- | :------ |
| tpIdx             | 0           | 1           | TIMEPULSE vs TIMEPULSE2 |
| freqPeriod        | 1 s         | 1 Hz        | unit depends on isFreq |
| pulseLenRatio     | 100 ms      | 0           | unit depends on isLength |
| freqPeriodLock    |             | 10 MHz      | depends on lockedOtherSet |
| pulseLenRatioLock |             | 50%         | depends on lockedOtherSet |
| active            | 1           | 1           | configuration is active |
| lockGnssFreq      | 1           | 1           | most precise but probably irrelevant |
| lockedOtherSet    | 0           | 1           | for recognizing no-lock situation |
| isFreq            | 0           | 1           | unit for freqPeriod(Lock) |
| isLength          | 1           | 0           | unit for pulsLenRatio(Lock) |
| alignToTow        | 1           | 1           | most precise but probably irrelevant |
| polarity          | 1           | 1           | 1 = rising edge |
| gridUtcGnss       | 1           | 1           | should be 0 (UTC) for astronomy |

The lockedOtherSet allows a no-lock situation to be made visible through the frequency and pulse length ratio of the timepulse. This seems useful for the LCD application.

## Configuration for LCD shutter

| ubx key           | TIMEPULSE   | TIMEPULSE2  | comment |
| :------------     | ----------- | ----------- | :------ |
| tpIdx             | 0           | 1           | TIMEPULSE vs TIMEPULSE2 |
| freqPeriod        | 1 Hz        | 16 Hz       | unit depends on isFreq |
| pulseLenRatio     | 50000       | 46875       | unit depends on isLength |
| freqPeriodLock    | 1 Hz        | 16 Hz       | depends on lockedOtherSet |
| pulseLenRatioLock | 50000       | 31250       | depends on lockedOtherSet |
| active            | 1           | 1           | configuration is active |
| lockGnssFreq      | 1           | 1           | most precise but probably irrelevant |
| lockedOtherSet    | 0           | 1           | for recognizing no-lock situation |
| isFreq            | 1           | 1           | unit for freqPeriod(Lock) |
| isLength          | 1           | 1           | unit for pulsLenRatio(Lock) |
| alignToTow        | 1           | 1           | most precise but probably irrelevant |
| polarity          | 1           | 1           | 1 = rising edge |
| gridUtcGnss       | 0           | 0           | should be 0 (UTC) for astronomy |

Other fields keep their default value.
isLength = 0 does not seem to work, so rather pulse duration in microseconds are provided.

**NB**: after entering the configurations above in the center of the UBX Configuration window, an additional command "CFG-MSG - Save configuration to non-volatile memory" has to be issued from the preset commands in the bottom-right corner, for obvious reasons.

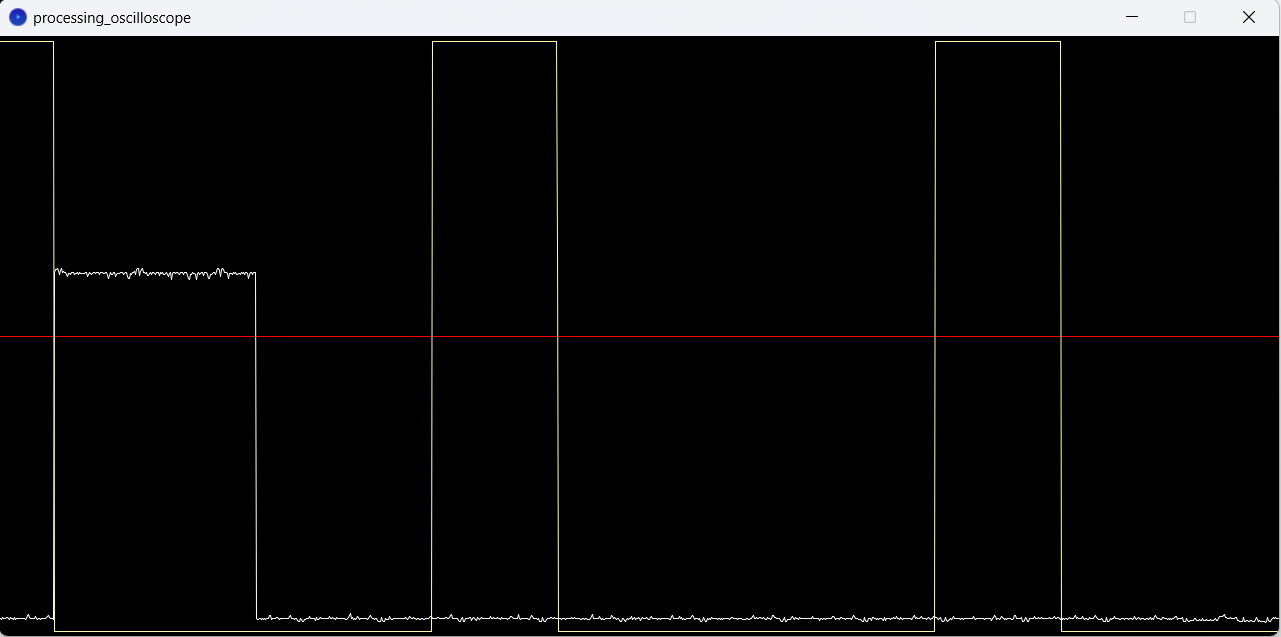
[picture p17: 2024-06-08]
doc/image/PIN3@SignalF.png

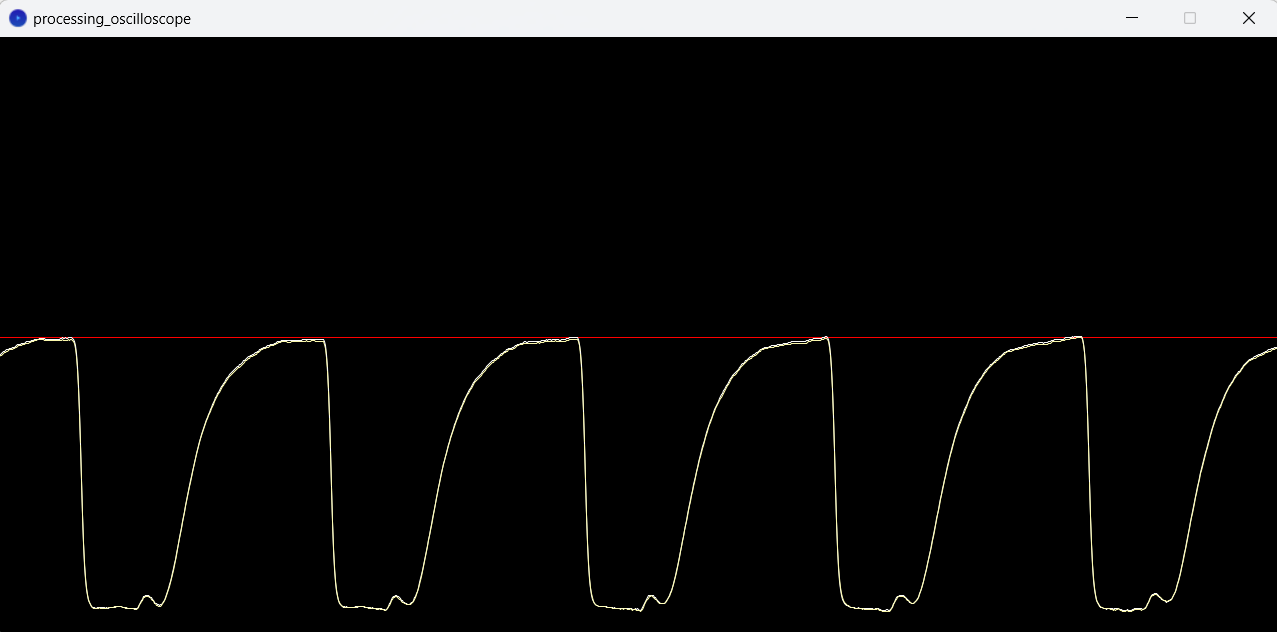
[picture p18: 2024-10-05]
doc/image/LCD-transmission-functiongenerator.png

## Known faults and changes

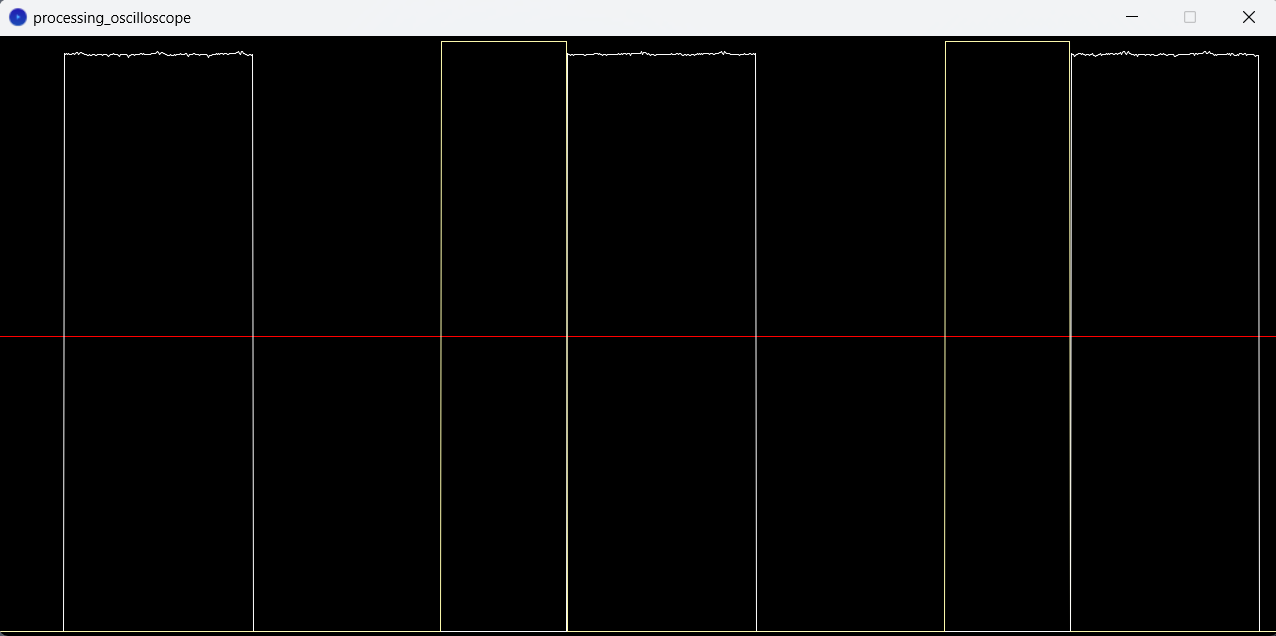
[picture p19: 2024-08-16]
doc/image/CMOS-vs-Arduino-issue.png

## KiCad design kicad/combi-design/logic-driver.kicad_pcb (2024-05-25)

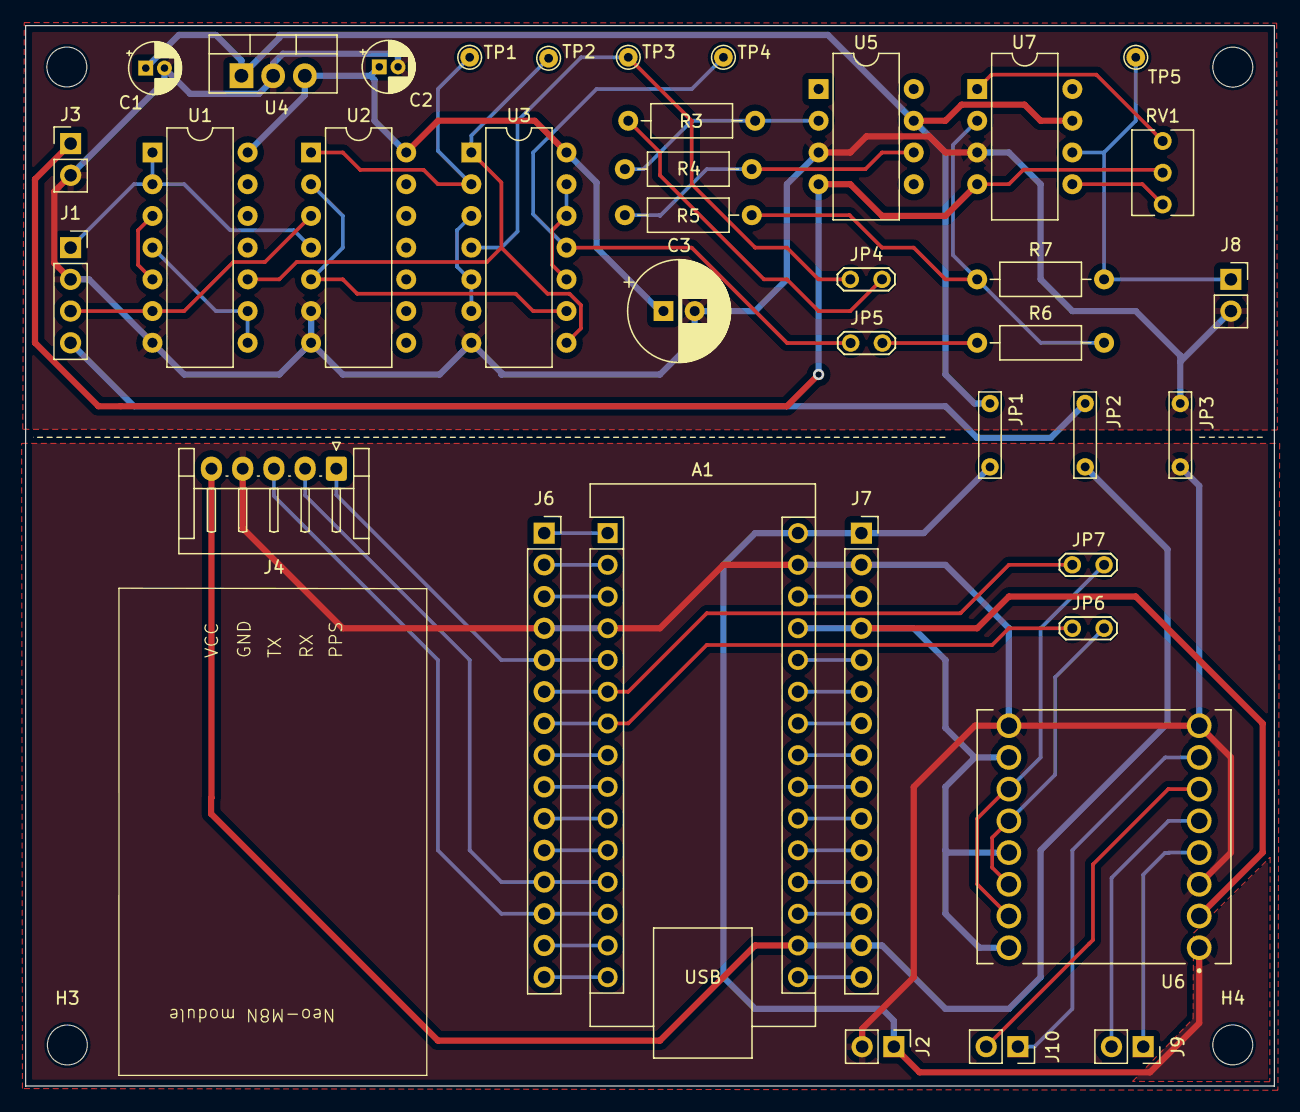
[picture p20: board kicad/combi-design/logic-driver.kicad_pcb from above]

Board: 2 copper layers, 100.0 x 84.9 mm, 42 parts (0 on the bottom side), 59 nets.

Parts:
A1: Nucleo32-STM32G431; Arduino_Nano
C1, C2: 2.2uF; CP_Radial_D4.0mm_P1.50mm
C3: 100uF; CP_Radial_D8.0mm_P2.50mm
H1, H2, H3, H4: MountingHole; MountingHole_3.2mm_M3_ISO14580
J1: Neo-M8T; PinSocket_1x04_P2.54mm_Vertical
J2, J3: Power in; PinHeader_1x02_P2.54mm_Vertical
J4: Onboard Neo_M8N; Neo-M8N_1x05_P2.50mm_Horizontal
J6: CN4; PinSocket_1x15_P2.54mm_Vertical
J7: CN3; PinSocket_1x15_P2.54mm_Vertical
J8: LCD-opamp; PinSocket_1x02_P2.54mm_Vertical
J9: LCD-A; PinSocket_1x02_P2.54mm_Vertical
J10: LCD-B; PinSocket_1x02_P2.54mm_Vertical
JP1: +12V; TestPoint_Bridge_Pitch5.08mm_Drill0.7mm
JP2: +3V3; TestPoint_Bridge_Pitch5.08mm_Drill0.7mm
JP3: GND; TestPoint_Bridge_Pitch5.08mm_Drill0.7mm
JP4, JP6: Pos pulses; TestPoint_2Pads_Pitch2.54mm_Drill0.8mm
JP5, JP7: Neg pulses; TestPoint_2Pads_Pitch2.54mm_Drill0.8mm
R3, R4, R5, R6, R7: 100k; R_Axial_DIN0207_L6.3mm_D2.5mm_P10.16mm_Horizontal
RV1: 100k; Potentiometer_Vishay_T73XW_Horizontal
TP1: Signal D; TestPoint_THTPad_D1.5mm_Drill0.7mm
TP2: Signal C; TestPoint_THTPad_D1.5mm_Drill0.7mm
TP3: Signal F; TestPoint_THTPad_D1.5mm_Drill0.7mm
TP4: Signal G; TestPoint_THTPad_D1.5mm_Drill0.7mm
TP5: Signal H; TestPoint_THTPad_D1.5mm_Drill0.7mm
U1, U3: 4011; CERDIP-14_W7.62mm_SideBrazed
U2: 4013; CERDIP-14_W7.62mm_SideBrazed
U4: LM7805_TO220; TO-220-3_Vertical
U5, U7: TL081; CERDIP-8_W7.62mm_SideBrazed
U6: ROB-14450; TB6612_Module_ROB-14450

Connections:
+L12V: C1.1, JP1.2 (B), U4.1 (VI), U5.7 (V+), U7.7 (V+)
-L12V: J3.1, RV1.2, U5.4 (V-), U7.4 (V-)
/+5V: C2.1, C3.1, U1.14 (VDD), U2.14 (VDD), U3.14 (VDD), U4.3 (VO)
/+12V: A1.30 (VIN), J2.1, J7.1, JP1.1 (A), U6.1 (VM)
/AVDD: A1.18 (AREF), J7.13
/L3V3: J1.4, JP2.2 (B)
/LGND: C1.2, C2.2, C3.2, J1.2, J3.2, J8.2, JP3.2 (B), U1.7 (VSS), U2.6 (S), U2.7 (VSS), U3.7 (VSS), U4.2 (GND), U5.3 (+), U7.3 (+)
/MCU_3V3: A1.17 (3V3), J4.5, J7.14, JP2.1 (A)
/MCU_5V: A1.27 (+5V), J7.4, U6.2 (VCC), U6.10 (PWMB), U6.13 (STBY), U6.16 (PWMA)
/NRSTA: A1.3 (~RESET), J6.3
/NRSTB: A1.28 (~RESET), J7.3
/PA0: A1.19 (A0), J7.12
/PA1: A1.20 (A1), J7.11
/PA2: A1.26 (A7), J7.5
/PA3: A1.21 (A2), J7.10
/PA4: A1.22 (A3), J7.9
/PA5/PB7: A1.23 (SDA/A4), J7.8
/PA6/PA15: A1.24 (SCL/A5), J7.7
/PA7: A1.25 (A6), J7.6
/PA8: A1.12 (D9), J4.2, J6.12
/PA9: A1.1 (TX1), J6.1
/PA10: A1.2 (RX1), J6.2
/PA11: A1.13 (D10), J4.3, J6.13
/PA12: A1.5 (D2), J4.1, J6.5
/PA15: A1.8 (D5), J6.8
/PB0: A1.6 (D3), J6.6, JP7.1 (A)
/PB3/PB8: A1.16 (SCK), J7.15
/PB4: A1.15 (MISO), J6.15
/PB5: A1.14 (MOSI), J6.14
/PB6: A1.9 (D6), J6.9
/PB7: A1.7 (D4), J6.7, JP6.1 (A)
/PF0: A1.10 (D7), J6.10
/PF1: A1.11 (D8), J6.11
GND: A1.4 (GND), A1.29 (GND), J2.2, J4.4, J6.4, J7.2, JP3.1 (A), U6.3 (GND), U6.8 (GND), U6.9 (GND)
unnamed: J1.1, U1.1, U1.2, U2.4 (R)
unnamed: J1.3, U1.6, U2.3 (C)
unnamed: J8.1, R7.2, TP5.1, U7.6
unnamed: J9.1, U6.4 (A01)
unnamed: J9.2, U6.5 (A02)
unnamed: J10.1, U6.7 (B01)
unnamed: J10.2, U6.6 (B02)
unnamed: JP4.1 (A), TP3.1, U3.4
unnamed: JP4.2 (B), R3.1
unnamed: JP5.1 (A), TP4.1, U3.11
unnamed: JP5.2 (B), R6.1
unnamed: JP6.2 (B), U6.12 (BI1), U6.14 (AI1)
unnamed: JP7.2 (B), U6.11 (BI2), U6.15 (AI2)
unnamed: R4.2, R5.1, U5.6
unnamed: RV1.1, U7.1 (NULL)
unnamed: RV1.3, U7.5 (NULL)
unnamed: TP2.1, U1.10, U3.1, U3.8
unnamed: U1.3, U1.5
unnamed: U1.4, U1.8, U1.9
unnamed: U2.2 (~Q), U2.5 (D), U3.9
unnamed: TP1.1, U2.1 (Q), U3.2
unnamed: U3.3, U3.5, U3.6
unnamed: U3.10, U3.12, U3.13
unnamed: R3.2, R4.1, U5.2 (-)
unnamed: R5.2, R6.2, R7.1, U7.2 (-)

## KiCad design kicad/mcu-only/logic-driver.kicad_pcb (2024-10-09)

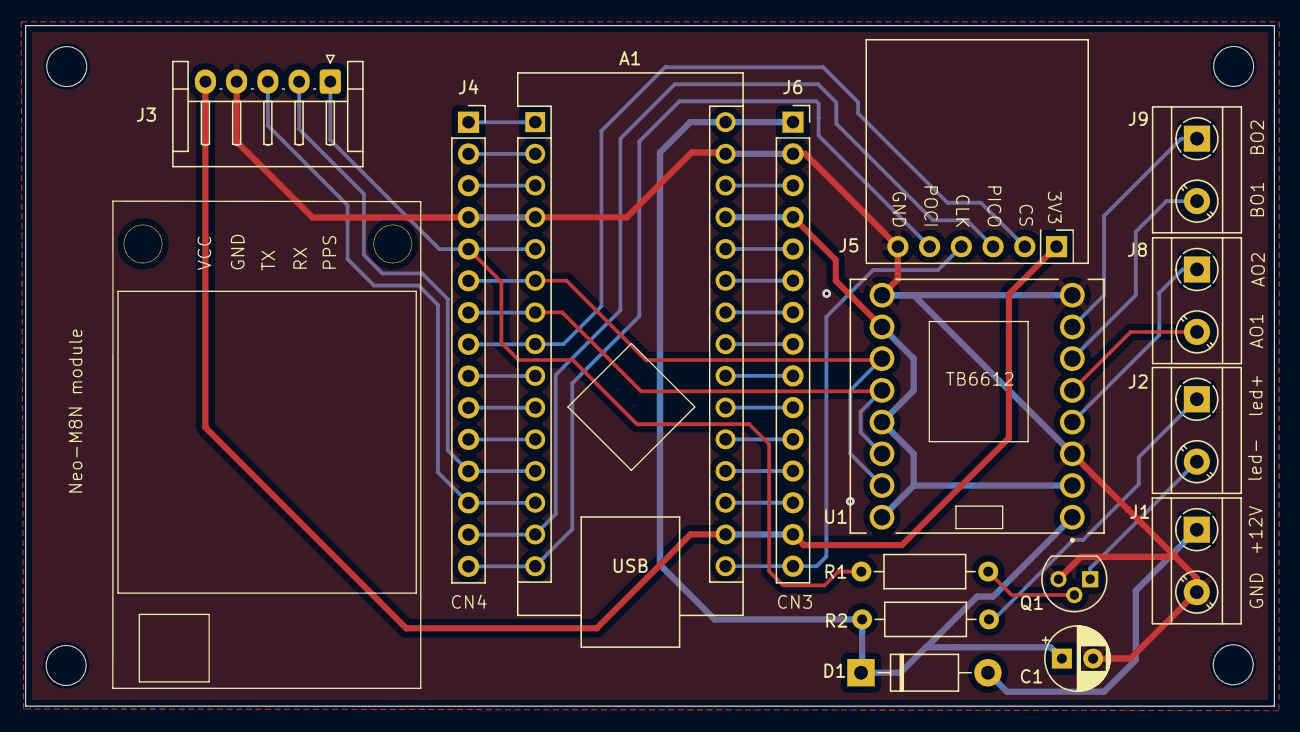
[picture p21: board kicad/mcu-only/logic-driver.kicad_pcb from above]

Board: 2 copper layers, 100.0 x 54.5 mm, 19 parts (0 on the bottom side), 37 nets.

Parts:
A1: STM32G431 / Arduino Nano; Arduino_Nano
C1: 47uF; CP_Radial_D5.0mm_P2.50mm
D1: 1N5818; D_DO-41_SOD81_P10.16mm_Horizontal
H1, H2, H3, H4: Hole; MountingHole_3.2mm_M3_ISO14580
J1: 12V/1A power in; TerminalBlock_RND_1x02_P5.00mm_Horizontal_Small_Courtyard
J2: PPS; TerminalBlock_RND_1x02_P5.00mm_Horizontal_Small_Courtyard
J3: Onboard Neo_M8N; Neo-M8N_1x05_P2.50mm_Horizontal
J4: CN4; PinSocket_1x15_P2.54mm_Vertical
J5: Onboard SD-card; SDcard_IPC_breakout_1x06_P2.54mm_Vertical
J6: CN3; PinSocket_1x15_P2.54mm_Vertical
J8: LCD-A; TerminalBlock_RND_1x02_P5.00mm_Horizontal_Small_Courtyard
J9: LCD-B; TerminalBlock_RND_1x02_P5.00mm_Horizontal_Small_Courtyard
Q1: BC547; TO-92
R1: 47k; R_Axial_DIN0207_L6.3mm_D2.5mm_P10.16mm_Horizontal
R2: 1k5; R_Axial_DIN0207_L6.3mm_D2.5mm_P10.16mm_Horizontal
U1: ROB-14450; TB6612_Module_ROB-14450

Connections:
/+12V: A1.30 (VIN), C1.1, D1.1 (K), J6.1, R2.1, U1.1 (VM)
/AVDD: A1.18 (AREF), J6.13
/MCU_3V3: A1.17 (3V3), J3.5, J5.1, J6.14
/MCU_5V: A1.27 (+5V), J6.4, U1.2 (VCC), U1.10 (PWMB), U1.13 (STBY), U1.16 (PWMA)
/NRSTA: A1.3 (~RESET), J4.3
/NRSTB: A1.28 (~RESET), J6.3
/PA0: A1.19 (A0), J6.12
/PA1: A1.20 (A1), J6.11
/PA2: A1.26 (A7), J6.5
/PA3: A1.21 (A2), J6.10
/PA4: A1.22 (A3), J6.9
/PA5/PB7: A1.23 (SDA/A4), J6.8
/PA6/PA15: A1.24 (SCL/A5), J6.7
/PA7: A1.25 (A6), J6.6
/PA8: A1.12 (D9), J3.2, J4.12
/PA9: A1.1 (TX1), J4.1
/PA10: A1.2 (RX1), J4.2
/PA11: A1.13 (D10), J3.3, J4.13
/PA12: A1.5 (D2), J3.1, J4.5, R1.1
/PA15: A1.8 (D5), J4.8, J5.2
/PB0: A1.6 (D3), J4.6, U1.11 (BI2), U1.15 (AI2)
/PB3/PB8: A1.16 (SCK), J5.4, J6.15
/PB4: A1.15 (MISO), J4.15, J5.5
/PB5: A1.14 (MOSI), J4.14, J5.3
/PB6: A1.9 (D6), J4.9
/PB7: A1.7 (D4), J4.7, U1.12 (BI1), U1.14 (AI1)
/PF0: A1.10 (D7), J4.10
/PF1: A1.11 (D8), J4.11
GND: A1.4 (GND), A1.29 (GND), C1.2, J1.2, J3.4, J4.4, J5.6, J6.2, Q1.3 (E), U1.3 (GND), U1.8 (GND), U1.9 (GND)
unnamed: D1.2 (A), J1.1
unnamed: J2.1, R2.2
unnamed: J2.2, Q1.1 (C)
unnamed: J8.1, U1.4 (A01)
unnamed: J8.2, U1.5 (A02)
unnamed: J9.1, U1.7 (B01)
unnamed: J9.2, U1.6 (B02)
unnamed: Q1.2 (B), R1.2

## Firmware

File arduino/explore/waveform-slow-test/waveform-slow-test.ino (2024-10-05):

/* Script that experiments with:
   - timing jitter from a free loop
   - timing jitter from an interrupt-based loop
   - writing two digital pins simultaneously

   It might be useful for certain tests as well
*/
const unsigned long blockMicros = 2000000;
const int zeroVal = 127;
const int pinNeg = 3;
const int pinPos = 4;
const byte NEG_MASK = B00000100;
const byte POS_MASK = B00010000;
const byte ZERO_MASK = B11101011;

unsigned long startMicros;
byte previousPinVals;


// Register settings, see: https://exploreembedded.com/wiki/AVR_Timer_programming
// Interrupt setting, see: https://circuitdigest.com/microcontroller-projects/arduino-timer-tutorial
// Arduino core AVR uses TIMER0 for millis()/micros()
// TIMER1 can be used if the servo library is not needed
// TIMER1 is configured to CTC mode (Clear Timer on Compare)
ISR(TIMER1_COMPA_vect)                   
{
  char buf[50];
  unsigned long relMicros = micros() - startMicros;
  ltoa(relMicros, buf, 10);
  Serial.write(buf);
  Serial.println(" TIMER1 interrupt occured!");
}

int switchPins(unsigned long diffMicros)
{
  long nHalfWaves = diffMicros / blockMicros;
  // Use the PORTD register to have pins 2 and 4 switch simultaneously
  // Some jitter is possible because the branches below follow a different sequence of instructions
  byte pinVals;
  if (nHalfWaves % 2 == 1) {
      pinVals = (PORTD & ZERO_MASK);
  } else if (nHalfWaves % 4 == 2) {
      pinVals = (PORTD & ZERO_MASK) | NEG_MASK;
  } else {
      pinVals = (PORTD & ZERO_MASK) | POS_MASK;
  }
  PORTD = pinVals;
  return pinVals;
}

// Note: Arduino UNO uses a cheap ceramic oscillator with +/- 0.5% frequency tolerance:
//    https://www.arrow.com/en/research-and-events/articles/oscillators-and-arduino-configurations-and-settings
void setup()
{
  pinMode(pinNeg, OUTPUT);
  pinMode(pinPos, OUTPUT);
  Serial.begin(2000000);
  startMicros = micros();
  previousPinVals = PORTD;

  // Testing TIMER1 interrupts
  TCCR1A = 0x00;
  TCCR1B = (1<<CS12);                // set the prescalar at 256
  TCCR1B |= (1 << WGM12);            // CTC mode (Clear Timer on Compare)
  OCR1A = 62499;                     // compare value for 1000ms delay
  TCNT1 = 0;                         // start value
  TIMSK1 |= (1<<OCIE1A);             // enable TIMER1 interrupts
}

void loop()
{
  // Without timers the delay visible on the serial console varies from 0 to 40 microseconds
  char buf[50];
  // Note: overflow does not interfere with small differences
  unsigned long relMicros = micros() - startMicros;
  byte pinVals = switchPins(relMicros);
  if (pinVals != previousPinVals) {
    ltoa(relMicros, buf, 10);
    Serial.write("New pin output at ");
    Serial.write(buf);
    Serial.write(": ");
    Serial.println(pinVals);
  }
  previousPinVals = pinVals;
}

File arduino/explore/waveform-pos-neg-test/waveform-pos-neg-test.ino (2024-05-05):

/* Script with experiments to possibly have the LCD shutter open faster (closing is fast by default):
   - block waveform that ends with a short pulse of inverted voltage
   - block waveform that alternates fast between positive ande negative continously
*/
const int pinNeg = 2;
const int pinPos = 4;
const byte NEG_MASK = B00000100;
const byte POS_MASK = B00010000;
const byte ZERO_MASK = B11101011;


int switchPins(int value)
{
  // Use the PORTD register to have pins 2 and 4 switch simultaneously
  // Some time jitter is possible because the branches below follow a different sequence of instructions
//  byte pinVals;
  if (value == 0) {
      digitalWrite(pinNeg, LOW);
      digitalWrite(pinPos, LOW);
      // pinVals = (PORTD & ZERO_MASK);
  } else if (value == -1) {
      digitalWrite(pinNeg, HIGH);
      digitalWrite(pinPos, LOW);
      // pinVals = (PORTD & ZERO_MASK) | NEG_MASK;
  } else {
      digitalWrite(pinNeg, LOW);
      digitalWrite(pinPos, HIGH);
      //pinVals = (PORTD & ZERO_MASK) | POS_MASK;
  }
//  PORTD = pinVals;
  return 0; //pinVals;
}

void setup()
{
  pinMode(pinNeg, OUTPUT);
  pinMode(pinPos, OUTPUT);
  Serial.begin(2000000);
}

void shortInverted()
{
  const int HALF_WAVE = 32;    // milliseconds
  const int INV_PULSE = 5000;  // microseconds
  switchPins(1);
  delay(HALF_WAVE);
// Commenting this out shows that the short pulse has no influence
// because successive pulses have the same shape
//  switchPins(-1);
  delayMicroseconds(INV_PULSE);
  switchPins(0);
  delay(HALF_WAVE);
  switchPins(-1);
  delay(HALF_WAVE);
  switchPins(1);
  delayMicroseconds(INV_PULSE);
  switchPins(0);
  delay(HALF_WAVE);  
}

void fastPositiveNegative()
{
  // The sequences of 2 ms alternating positive and negative pulses neither
  // have any influence on the opacity waveform of the LCD-shutter, compared
  // to a simple 32 ms halfwave block waveform.
  const int HALF_WAVE = 32;  // milliseconds
  const int PULSE = 2;       // milliseconds
  for (int i=0; i<HALF_WAVE/(2*PULSE); i++) {
    switchPins(1);
    delay(PULSE);
    switchPins(-1);
    delay(PULSE);
  }
  switchPins(0);
  delay(HALF_WAVE);
  for (int i=0; i<HALF_WAVE/(2*PULSE); i++) {
    switchPins(1);
    delay(PULSE);
    switchPins(-1);
    delay(PULSE);
  }
  switchPins(0);
  delay(HALF_WAVE);
}

void loop()
{
  while(true)
  {
    // Uncomment one of the modes below
    //pshortInverted();
    fastPositiveNegative();
  }
}

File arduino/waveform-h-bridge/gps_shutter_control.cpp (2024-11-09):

/*
Script for generating digital signals as input for an H-bridge driver of an LCD-shutter.
The signals have a specific pattern useful for meteor photography and are synced
to the 1 Hz GPS TIMEPULSE signal, also called PPS signal. For this, the script
applies three mechanisms:
1. Shortly after each GPS pulse, so during the blanking period of a 1 second cycle, a
   new train of 16 pulses is started that initially is synced very closely to the GPS
   signal.
2. The MCU frequency is measured during a relatively long period (>= 60 seconds) with
   the GPS pulses as an accurate reference. After that, the timing of the train of 15
   pulses is done using this calibrated MCU frequency. This significantly improves
   the syncing of the pulse train at the end of a cycle. Note that the Arduino clock
   has a ceramic resonator with a frequency of 16 MHz +/- 0.5% (so, not very accurate).
3. Timing of the train of 15 pulses is done with interrupts triggered by a hardware
   timer of the Arduino MCU, which has a granularity of 4 microseconds. After
   switching the outputs for 32 times during a 1 second cycle, this results in a
   maximum phase difference with the GPS signal of 128 microseconds (after applying
   mechanism 2). Mechanism 3 could further reduce the phase difference by varying the
   individual durations in a train of 16 pulses such that the sum of the residuals is
   minimal.

Without a GPS signal the script operates in a free running mode generating 16 pulses
per second using the calibratedFreq variable as a reference (boot value can be edited).

Documentation used as input for this script:
 - register settings:  https://exploreembedded.com/wiki/AVR_Timer_programming
 - interrupt settings: https://circuitdigest.com/microcontroller-projects/arduino-timer-tutorial
 - MCU clock accuracy: https://www.arrow.com/en/research-and-events/articles/oscillators-and-arduino-configurations-and-settings

The code below uses micros() for time keeping based on the MCU clock. The Arduino library uses a 32-bit
counter for the micros() function, which overflows after about 70 minutes. Therefore, only time differences
between successive micros() calls are used, which are always correct irrespective of any overflow that
occurred between the two calls.

The code below implements a state machine with the states described below (stored as iGpsPulse).
|-> INIT - entered at the start or after receiving an out-of-phase GPS pulse
|    |
|    |
|    |-> ZERO - entered when receiving the zeroth GPS pulse while being in the INIT state
|        |
|        |
|--------|-> STABLE - entered when receiving GPS pulse number N_STABLE while being in the FIRST state
|            |
|            |
|            |-> CALIBRATED - entered when receiving GPS pulse number N_CALIBRATE while being in the STABLE state
|----------------|

In the STABLE and CALIBRATED states the pulse trains are locked to the GPS signal and the following events occur
each second (see the signal diagram in the README of the repo root):
1. just before the GPS pulse arrives, a new pulse train has started with iHalfWave = 32. Outside the locked state
   this would be a positive electrical voltage using POS_MASK, but in the locked state this triggers a specific
   condition resulting in an electrical shortcut state using HIGH_MASK.
2. the GPS pulse arrives and sets gpsHit to true
3. the shutter_control loop detects the gspHit state and starts correcting small phase differences by manipulating
   the value of TCNT1. Both leaving the control logic, iHalfWave should be zero.
*/
#define DEBUG_LOG
#undef DEBUG_LOG                                      // Outcomment to enable debug logging

#include <arduino.h>
#include "gps_shutter_control.h"

// Constant values
const int PIN_GPS = 2;                                // Match with hardware connection
const int PIN_NEG = 3;                                // Match with hardware connection, odd negative pulses
const int PIN_POS = 4;                                // Match with hardware connection, even positive pulses
const byte NEG_MASK = (1 << 3);                       // Precalculate for fast interrupt handling
const byte POS_MASK = (1 << 4);                       // Precalculate for fast interrupt handling
const byte HIGH_MASK = NEG_MASK | POS_MASK;           // Additional mask for H-bridge driver
const byte ZERO_MASK = 255 & ~NEG_MASK & ~POS_MASK;   // Precalcualte for fast interrupt handling
const int MCU_MHZ = 16;                               // From Arduino specs
const int N_WAVE = 16;                                // The shutter frequency
const int N_HALF_WAVE = 32;                           // Twice the shutter frequency
const int PRESCALER = 64;                             // Prescaler value to be set for TIMER1
const int TICK_MICROS = 4;                            // TIMER1 resolution with prescaler at 64
const int N_INIT = -1;                                // iGpsPulse value for the INIT state (no GPS pulse received)
const int N_ZERO = 0;                                 // iGpsPulse value for the ZERO state (first GPS pulse interval started)
const int N_STABLE = 10;                              // iGpsPulse value for the STABLE state: starting second markers (short GPS calibration interval)
const int N_CALIBRATE = 60;                           // iGpsPulse value for the CALIBRATED state (< 4200): GPS-calibrated second markers
const int TIMER_SAFETY = 2;                           // For being sure the duration of the pulse train < 1.000000 second
                                                      // This is for 1 wave period, so impact = N * 16 * 4 = N * 64 microseconds

// Global variables modified in interrupt routines
volatile bool gpsHit = false;                         // Set by the gpsIn interrupt only and cleared after processing
volatile unsigned long lastGpsMicros;                 // Set by the gpsIn interrupt only and ignored before gpsHit = true
volatile unsigned long iHalfWave = 0;                 // Phase of shutter waveform in terms of block half waves
volatile unsigned long iIsr = 0;                      // For monitoring

// Global variables related to and depending on calibration
int shutPercentage;                                   // Value passed to setup_shutter_control()
int compensationTicks;                                // Code execution duration from time measurement to timer adjustment
unsigned long calibratedFreq = 1000000 * MCU_MHZ;     // Overwritten by initial calibration after 10 GPS pulse intervals
unsigned int waveTicks;                               // Number of ticks of 1 wave of 16 Hz (depends on auto-calibration)
unsigned int ocr1aShut;                               // Precalculated timer value based on shutPercentage and auto-calibration
unsigned int ocr1aOpen;                               //       ,,        ,,    ,,    ,,          ,,                  ,,

// Global variables related to the lock state
unsigned long iGpsPulse = -1;                         // Number of successive GPS pulse intervals counted for stabilization and calibration
unsigned long prevGpsMicros;                          // For checking timely arrival of current iGpsPulse
unsigned long gpsStartMicros;                         // Start time of a sequence of successive GPS pulses

// Global character buffer for sprintf() + Serial.println()
const int S = 90;
char s[S];

// Global variable related to debug logging
#ifdef DEBUG_LOG
const int NLOG = 100;                                 // About 3 seconds of hispeed logging
volatile int iLog = -960;                             // This logging starts after 30 seonds of operation
volatile unsigned long logIsr[NLOG];                  // Stores iIsr values
volatile unsigned long logHalf[NLOG];                 // Stores iHalfWave values
volatile unsigned long logMicros[NLOG];               // Stores micros()
#endif

/*
 * In the run_shutter_control() loop lastGpsMicros is used:
 *  - to derive the GPS lock state
 *  - to calibrate the MCU clock
 * The gpsHit variable is used to trigger the control logic in the run_shutter_control() loop.
 */
void gpsIn()
{
  cli();                                  // disable interrupts for making the value changes below in an atomic way
  lastGpsMicros = micros();               // the micros() value can be reliably read on entry of an ISR
  gpsHit = true;
  iIsr = 0;
  sei();
}
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

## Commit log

2023-11-28 Adds initial documentation and placeholder for Arduino script
    [logic-driver.kicad_sch]
2023-12-12 just noticed it was supposed to be 16, not 32Hz
2024-01-12 Rewires the D-flipflop divider to have signal C in phase with TIMEPULSE
    [logic-driver.kicad_sch]
2024-01-12 Puts arduino file in folder
2024-01-12 Adds Arduino oscilloscope files
2024-02-17 Updates the electronic schema
    [logic-driver.kicad_sch]
2024-03-10 Adds unfinished Arduino R4 script for slow 3-level waveform on A0 DAC output
2024-03-10 Adds Arduino slow waveform with two dig outputs; still without timers
2024-03-17 Adds arduino script for measuring loop jitter
2024-03-22 Adds new Arduino test waveforms for attempts on faster opening the LCD-shutter
2024-04-01 Redesigns the main two-pin waveform, still with errors but promising
2024-04-13 Update schema regarding voltage follower
    [logic-driver.kicad_sch]
2024-05-05 Improves two pin waveform regarding stability and consistency
2024-05-25 Adds rened kicad circuit and the kicad PCB design
    [logic-driver.kicad_pcb, logic-driver.kicad_sch]
2024-05-25 Updates electric circuit diagram
2024-06-08 Add documentation for programming the Arduino
2024-06-23 Adds documentation for measuring with the Arduino oscilloscope script
2024-06-29 Updates arduino docs with the changed figures
2024-06-29 Adds preliminary calibration after 10 seconds of stabilization
2024-06-29 Updates Arduino programming docs
2024-08-25 Reorganizes arduino folder
2024-09-01 Adds Arduino code for GPS time + latlon readout
2024-10-05 Adds blinking LED script
2024-10-09 Adds KiCAD design files for the mcu-only PCB
    [logic-driver.kicad_pcb, logic-driver.kicad_sch]
2024-10-18 Introduces additional INIT state and prints VERSION
2024-10-19 Fixes chipselect pin for AliExpress SD card reader
